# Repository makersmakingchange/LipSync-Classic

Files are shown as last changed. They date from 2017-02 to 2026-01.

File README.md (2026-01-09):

# LipSync Classic

> [!IMPORTANT]
**As of 2024-Feb-08, this version of the LipSync is now obsolete and has been replaced by the [LipSync 4](https://github.com/makersmakingchange/LipSync).** 

The LipSync Classic is an assistive technology device that allows quadriplegics and other people with limited hand function to use touchscreen mobile devices, tablets, and computers by manipulation of a mouth-operated joystick with integrated sip and puff controls. This is an Open-Source Hardware project, so the Lipsync can be made at the community level for less than $300.

## Compatibility 

 <table style="width:100%">
  <tr>
    <th>Operating Systems</th>
    <th>Version</th>
    <th>Release</th>
    <th>Additional Information</th>
  <tr>
    <td>iOS</td>
    <td>13.1</td>
    <td>September 19,2019</td>
    <td>Compatible with iPhone 7 and newer versions (Requires USB to Lightning or USB to USB-C Adapter)</td>
  </tr>
  <tr>
    <td>Windows</td>
    <td>XP,7,10</td>
    <td>2001</td>
    <td>Compatible with Windows XP and newer versions</td>
  </tr>
  <tr>
    <td>Android</td>
    <td>4-9</td>
    <td>Released 2013</td>
    <td>Compatible with Android 4 and newer versions (Requires USB On-The-Go)</td>
  </tr>
  <tr>
    <td>MacOS</td>
    <td>10</td>
    <td>Released 2000</td>
    <td>Compatible with Mac OS X 10.0 and newer versions</td>
  </tr>
  </table> 

## Download

 <table style="width:100%">
  <tr>
    <th>Resource</th>
    <th>Version</th>
    <th>Format</th>
    <th>Link</th>
  </tr>
    <tr>
    <td>LipSync All</td>
    <td>3.0</td>
    <td>ZIP</td>
    <td><a href="https://github.com/makersmakingchange/LipSync/archive/refs/heads/main.zip">LipSync.zip</a></td>
  </tr>
  <tr>
    <td>LipSync Assembly Guide</td>
    <td>1.6</td>
    <td>PDF</td>
    <td><a href="https://github.com/makersmakingchange/LipSync/blob/main/Documentation/LipSync_Assembly_Guide.pdf">LipSync_Assembly_Guide.pdf</a></td>
  </tr>
  <tr>
    <td>LipSync Startup Guide</td>
    <td>1.8</td>
    <td>PDF</td>
    <td><a href="https://github.com/makersmakingchange/LipSync/blob/main/Documentation/LipSync_Startup_Guide.pdf">LipSync_Startup_Guide.pdf</a></td>
  </tr>
  <tr>
    <td>LipSync User Guide</td>
    <td>1.3</td>
    <td>PDF</td>
    <td><a href="https://github.com/makersmakingchange/LipSync/blob/main/Documentation/LipSync_User_Guide.pdf">LipSync_User_Guide.pdf</a></td>
  </tr>
  <tr>
     <td>LipSync Mounting Guide</td>
     <td>1.0</td>
     <td>PDF</td>
     <td><a href="https://github.com/makersmakingchange/LipSync/blob/main/Documentation/LipSync_Mounting_Guide.pdf">LipSync_Mounting_Guide.pdf</a></td>
  </tr>
  <tr>
    <td>LipSync BOM (XLSX)</td>
    <td>September 1, 2021</td>
    <td>XLSX</td>
    <td><a href="https://github.com/makersmakingchange/LipSync/blob/main/Documentation/LipSync_BOM.xlsx">LipSync_BOM.xlsx</a></td>
  </tr>
  <tr>
    <td>LipSync BOM (CSV)</td>
    <td>September 1, 2021</td>
    <td>CSV</td>
    <td><a href="https://github.com/makersmakingchange/LipSync/blob/main/Documentation/LipSync_BOM.csv">LipSync_BOM.csv</a></td>
  </tr>
  <tr>
    <td>LipSync Firmware</td>
    <td>3.0</td>
    <td>INO</td>
    <td><a href="https://raw.githubusercontent.com/makersmakingchange/LipSync/main/Software/LipSync_Firmware/LipSync_Firmware.ino">LipSync_Firmware.ino</a></td>
  </tr>
  <tr>
    <td>LipSync Interface Board Layout</td>
    <td>2.71</td>
    <td>BRD</td>
    <td><a href="https://raw.githubusercontent.com/makersmakingchange/LipSync/main/Hardware/PCB_design/Eagle/LipSync_Interface_Board/LipSync_Interface_Board.brd">LipSync_Interface_Board.brd</a></td>
  </tr>
  <tr>
    <td>LipSync Interface Board Schematic</td>
    <td>2.71</td>
    <td>SCH</td>
    <td><a href="https://raw.githubusercontent.com/makersmakingchange/LipSync/main/Hardware/PCB_design/Eagle/LipSync_Interface_Board/LipSync_Interface_Board.sch">LipSync_Interface_Board.sch</a></td>
  </tr>
  <tr>
    <td>JLCPCB LipSync Interface Board Gerber</td>
    <td>2.71</td>
    <td>ZIP</td>
    <td><a href="https://github.com/makersmakingchange/LipSync/raw/main/Hardware/PCB_design/Gerber/LipSync_Interface_Board/JLCPCB_LipSync_Interface_Board.zip">JLCPCB_LipSync_Interface_Board.zip</a></td>
  </tr>
  <tr>
    <td>OSHPark LipSync Interface Board Gerber</td>
    <td>2.71</td>
    <td>ZIP</td>
    <td><a href="https://github.com/makersmakingchange/LipSync/raw/main/Hardware/PCB_design/Gerber/LipSync_Interface_Board/OSHPark_LipSync_Interface_Board.zip">OSHPark_LipSync_Interface_Board.zip</a></td>
  </tr>
  <tr>
    <td>PCBWay LipSync Interface Board Gerber</td>
    <td>2.71</td>
    <td>ZIP</td>
    <td><a href="https://github.com/makersmakingchange/LipSync/raw/main/Hardware/PCB_design/Gerber/LipSync_Interface_Board/PCBWay_LipSync_Interface_Board.zip">PCBWay_LipSync_Interface_Board.zip</a></td>
  </tr>
  <tr>
    <td>Seeed Fusion LipSync Interface Board Gerber</td>
    <td>2.71</td>
    <td>ZIP</td>
    <td><a href="https://github.com/makersmakingchange/LipSync/raw/main/Hardware/PCB_design/Gerber/LipSync_Interface_Board/Seeed_Fusion_LipSync_Interface_Board.zip">Seeed_Fusion_LipSync_Interface_Board.zip</a></td>
  </tr>
  <tr>
    <td rowspan="9">Housing_design</td>
    <td rowspan="9">3.0</td>
    <td rowspan="9">STL</td>
    <td><a href="https://github.com/makersmakingchange/LipSync/blob/main/Hardware/Housing_design/LipSync_Button.stl">LipSync_Button.STL</a></td>
  </tr>
  <tr>
  <td><a href="https://github.com/makersmakingchange/LipSync/blob/main/Hardware/Housing_design/LipSync_Front_Housing.STL">LipSync_Front_Housing.STL</a></td>
  </tr>
  <tr>
	<td><a href="https://github.com/makersmakingchange/LipSync/blob/main/Hardware/Housing_design/LipSync_Joystick_Base.STL">LipSync_Joystick_Base.STL</a></td>
</tr>
<tr>
  <td><a href="https://github.com/makersmakingchange/LipSync/blob/main/Hardware/Housing_design/LipSync_Joystick_Front.STL">LipSync_Joystick_Front.STL</a></td>
</tr>
<tr>
  <td><a href="https://github.com/makersmakingchange/LipSync/blob/main/Hardware/Housing_design/LipSync_Joystick_Rocker.STL">LipSync_Joystick_Rocker.STL</a></td>
</tr>
<tr>
    <td><a href="https://github.com/makersmakingchange/LipSync/blob/main/Hardware/Housing_design/Optional/LipSync_Joystick_Jig.STL">LipSync_Joystick_Jig.STL</a></td>
</tr>
<tr>
  <td><a href="https://github.com/makersmakingchange/LipSync/blob/main/Hardware/Housing_design/LipSync_Rear_Housing.STL">LipSync_Rear_Housing.STL</a></td>
</tr>
<tr>
  <td><a href="https://github.com/makersmakingchange/LipSync/blob/main/Hardware/Housing_design/3D_Print_Settings.txt">3D_Print_Settings.txt</a></td>
</tr>
</table> 

## Resources

<table style="width:100%">
  <tr>
    <th>Resource</th>
    <th>Link</th>
  </tr>
  <tr>
    <td>LipSync Firmware and Calibration Video</td>
    <td><a href="https://www.youtube.com/watch?v=RnpA24WH0Qk">Video</a></td>
  <tr>
    <td>LipSync Joystick Calibration Video</td>
    <td><a href="https://www.youtube.com/watch?v=Daf-54y6SBg">Video</a></td>
  </tr>
    <tr>
    <td>LipSync Build Video</td>
    <td><a href="https://www.youtube.com/watch?v=lBXpbkp5DW4&list=PLhoPg9bDvBR4CSFRfNbQ87ALnfaHOyM3C">Video</a></td>
  </tr>
</table> 

## License
Copyright (c) 2016-2024 Neil Squire / Makers Making Change.

This repository describes Open Hardware:
 - Everything needed or used to design, make, test, or prepare the LipSync Classic is licensed under the [CERN 2.0 Weakly Reciprocal license (CERN-OHL-W v2) or later](https://cern.ch/cern-ohl ) .
 - All software is under the [GNU General Public License v3.0 (GPL-3.0)](https://www.gnu.org/licenses/gpl.html).
 - Accompanying material such as instruction manuals, videos, and other copyrightable works that are useful but not necessary to design, make, test, or prepare the LipSync are published under a [Creative Commons Attribution-ShareAlike 4.0 license (CC BY-SA 4.0)](https://creativecommons.org/licenses/by-sa/4.0/) .

You may redistribute and modify this documentation and make products using it under the terms of the [CERN-OHL-W v2](https://cern.ch/cern-ohl).
This documentation is distributed WITHOUT ANY EXPRESS OR IMPLIED WARRANTY, INCLUDING OF MERCHANTABILITY, SATISFACTORY QUALITY AND FITNESS FOR A PARTICULAR PURPOSE.
Please see the CERN-OHL-W v2 for applicable conditions.

Source Location: https://github.com/makersmakingchange/LipSync-Classic

## Attribution

The LipSync was designed by Neil Squire Society / Makers Making Change. The initial development of a 3D printable LipSync was supported by the Google Impact Challenge: Disabilities grant from Google.org. Further development was supported through the Government of Canada's Innovation Science and Economic Development Assistive Technology Program. These and other funders have also enabled Neil Squire / Makers Making Change to deploy numerous LipSyncs to users at reduced cost.

The LipSync firmware utilizes the Arduino development platform, an open-source electronics platform based on easy-to-use hardware and software. Arduino is developed and maintained by the Arduino community, and the project wouldn't be possible without their contributions. Arduino is a registered trademark of Arduino AG. For more information about Arduino and to contribute to the community, visit the official Arduino website at www.arduino.cc.

### Contributors

Numerous Neil Squire staff, users, and volunteers have contribued to the development of the LipSync. 

 - Derrick Andrews
 - Ivan Gourlay
 - Jake McIvor
 - Kristina Mok
 - Milad Hajihassan

----

<!-- ABOUT MMC START -->
## About Makers Making Change
[Makers Making Change Logo](https://www.makersmakingchange.com/)

Makers Making Change is a program of [Neil Squire](https://www.neilsquire.ca/), a Canadian non-profit that uses technology, knowledge, and passion to empower people with disabilities.

Makers Making Change leverages the capacity of community based Makers, Disability Professionals and Volunteers to develop and deliver affordable Open Source Assistive Technologies.

 - Website: [www.MakersMakingChange.com](https://www.makersmakingchange.com/)
 - GitHub: [makersmakingchange](https://github.com/makersmakingchange)
 - Bluesky: [@makersmakingchange.bsky.social](https://bsky.app/profile/makersmakingchange.bsky.social)
 - Instagram: [@makersmakingchange](https://www.instagram.com/makersmakingchange)
 - Facebook: [makersmakechange](https://www.facebook.com/makersmakechange)
 - LinkedIn: [Neil Squire Society](https://www.linkedin.com/company/neil-squire-society/)
 - Thingiverse: [makersmakingchange](https://www.thingiverse.com/makersmakingchange/about)
 - Printables: [MakersMakingChange](https://www.printables.com/@MakersMakingChange)

### Contact Us
For technical questions, to get involved, or to share your experience we encourage you to [visit our website](https://www.makersmakingchange.com/) or [contact us](https://www.makersmakingchange.com/s/contact).
<!-- ABOUT MMC END -->

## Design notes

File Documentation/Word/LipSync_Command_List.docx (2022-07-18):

## LipSync Mouse Command List

Command | Success Response | Failure Response | Description
SETTINGS | SUCCESS,0:SETTINGS | FAIL,{N}: Command | Enter Settings mode
EXIT | SUCCESS,0:EXIT | FAIL,{N}: Command | Exit Settings mode
MN,0:0 | SUCCESS,0:MN,0:1 | FAIL,{N}:Command | Get Model number (1=Mouse)
VN,0:0 | SUCCESS,0:VN,0:V{N.NN} | FAIL,{N}:Command | Get version number (V{N.NN})
SS,0:0 | SUCCESS,0:SS,0:{Cursor Speed Level} | FAIL,{N}:Command | Get the mouse cursor speed value (Level)
SS,1:{Cursor Speed Level:0-10} | SUCCESS,0:SS,1:{Cursor Speed Level} | FAIL,{N}:Command | Set the mouse cursor speed value (Level)
| MANUAL,0:SS,1:{Cursor Speed Level} | | Set the mouse cursor speed value (Level)
PT,0:0 | SUCCESS,0:PT,0:{Threshold 5% to 50%}:{Nominal Pressure V*100} | FAIL,{N}:Command | Get puff pressure threshold (threshold 5% to 50%) (Nominal Pressure)
PT,1:{threshold 10% to 50%} | SUCCESS,0:PT,1:{Threshold 5% to 50%}:{ Nominal Pressure V*100} | FAIL,{N}:Command | Set puff pressure threshold (threshold 5% to 50%) (Nominal Pressure)
ST,0:0 | SUCCESS,0:PT,0:{Threshold 5% to 50%}:{Nominal Pressure V*100} | FAIL,{N}:Command | Get sip pressure threshold (threshold 5% to 50%) (Nominal Pressure)
ST,1:{threshold 5% to 50%} | SUCCESS,0:PT,1:{Threshold 5% to 50%}:{ Nominal Pressure V*100} | FAIL,{N}:Command | Set sip pressure threshold (threshold 5% to 50%) (Nominal Pressure)
PV,0:0 | SUCCESS,0:PV,0:{Nominal Pressure} | FAIL,{N}:Command | Get pressure value (Nominal Pressure)
RA,0:0 | SUCCESS,0:RA,0:{Rotation Angle} | FAIL,{N}:Command | Get rotation angle (deg)
RA,1:{Angle: 0-359} | SUCCESS,0:RA,1:{Rotation Angle} | FAIL,{N}:Command | Set rotation angle (0,90,180,270 deg)
DM,0:0 | SUCCESS,0:DM,0:{Debug Mode} | FAIL,{N}:Command | Get debug mode value ( 0=debug mode disabled,1=debug mode enabled)
DM,1:0 | SUCCESS,0:DM,1:0 | FAIL,{N}:Command | Set debug mode value to 0 (Disabled)
DM,1:1 | SUCCESS,0:DM,1:1 | FAIL,{N}:Command | Set debug mode value to 1 (Enabled)
| LOG,1:{0,0,0,xHighNeutral,xLowNeutral,yHighNeutral,yLowNeutral} | | Log initialization values once if debug mode is enabled
| LOG,2:{0,0,0,xHighMax,xLowMax,yHighMax,yLowMax} | | Log calibration values once if debug mode is enabled
| LOG,3:{x,y,action,xHigh,xLow,yHigh,yLow} | | Log cursor and FSR values if debug mode is enabled until debug mode is disabled
IN,0:0 | SUCCESS,0:IN,0:{xHighNeutral,xLowNeutral,yHighNeutral,yLowNeutral} | FAIL,{N}:Command | Get joystick initialization values (xHighNeutral,xLowNeutral,yHighNeutral,yLowNeutral)
IN,1:1 | SUCCESS,0:IN,1:{xHighNeutral,xLowNeutral,yHighNeutral,yLowNeutral} | FAIL,{N}:Command | Perform joystick initialization using command (xHighNeutral,xLowNeutral,yHighNeutral,yLowNeutral)
| MANUAL,0:IN,1:{xHighNeutral,xLowNeutral,yHighNeutral,yLowNeutral} | | Perform joystick initialization using push button or sip/puff (xHighNeutral, xLowNeutral,yHighNeutral,yLowNeutral)
JV,0:0 | SUCCESS,0:JV,0:{xHigh,xLow,yHigh,yLow} | FAIL,{N}:Command | Get joystick FSR values: {xHigh,xLow,yHigh,yLow}
CA,0:0 | SUCCESS,0:CA,0:{xHighMax,xLowMax,yHighMax,yLowMax} | FAIL,{N}:Command | Get joystick calibration values (xHighMax,xLowMax,yHighMax,yLowMax)
CA,1:1 | SUCCESS,0:CA,1:0 | FAIL,{N}:Command | Perform joystick calibration using command
| SUCCESS,0:CA,1:1 | FAIL,{N}:Command | Perform joystick calibration using command (Step 1)
| SUCCESS,0:CA,1:2 | FAIL,{N}:Command | Perform joystick calibration using command (Step 2)
| SUCCESS,0:CA,1:3 | FAIL,{N}:Command | Perform joystick calibration using command (Step 3)
| SUCCESS,0:CA,1:4 | FAIL,{N}:Command | Perform joystick calibration using command (Step 4)
| SUCCESS,0:CA,1:5:{xHighMax,xLowMax,yHighMax,yLowMax} | FAIL,{N}:Command | Perform joystick calibration using command (Step 5) (xHighMax,xLowMax,yHighMax,yLowMax)
| MANUAL,0:CA,1:0 | | Perform joystick calibration using push button
| MANUAL,0:CA,1:1 | | Perform joystick calibration using push button (Step 1)
| MANUAL,0:CA,1:2 | | Perform joystick calibration using push button (Step 2)
| MANUAL,0:CA,1:3 | | Perform joystick calibration using push button (Step 3)
| MANUAL,0:CA,1:4 | | Perform joystick calibration using push button (Step 4)
| MANUAL,0:CA,1:5:{xHighMax,xLowMax,yHighMax,yLowMax} | | Perform joystick calibration using push button (Step 5) (xHighMax,xLowMax,yHighMax,yLowMax)
CT,0:0 | SUCCESS,0:CT,0:{changeTolerance} | FAIL,{N}:Command | Get drift change tolerance value
CT,1: {Change Tolerance: 0-30} | SUCCESS,0:CT,1:{changeTolerance} | FAIL,{N}:Command | Set drift change tolerance value
MP,0:0 | SUCCESS,0:MP,0:{NNNNNN} | FAIL,{N}:Command | Get Button mapping ( Example: SUCCESS,0:MP,0:123465)
MP,1: {NNNNNN} | SUCCESS,0:MP,1:{NNNNNN} | FAIL,{N}:Command | Set Button mapping ( Example: MP,1:123465)
SL,0:0 | SUCCESS,0:SL,0:{Scroll Speed Level} | FAIL,{N}:Command | Get the mouse scroll speed value (Level)
SL,1:{Scroll Speed Level:0-10} | SUCCESS,0:SL,1:{Scroll Speed Level} | FAIL,{N}:Command | Set the mouse scroll speed value (Level)
FR,1:{Rest Type: 0-1} | SUCCESS,0:FR,1:{Reset Type: 0-1} | FAIL,{N}:Command | Perform factory reset (0 = Hard Reset , 1 = Soft Reset)

## API Format

The API format which includes the end-point, command ,and the parameters.

## Response Code

Response Status | Response Code | Description
SUCCESS | 0 | The command has successfully performed.
FAIL | 0 | The serial API mode is not enabled. Please enter the serial API mode.
FAIL | 1 | The requested command does not exist. Returns the response code and the requested parameter.
FAIL | 2 | The requested command exists, but the entered parameter is in incorrect format. Returns the response code and the requested parameter.
FAIL | 3 | The requested command exists, but the entered parameter is out of range. Returns the response code and the current value stored in the EEPROM.

## Input Actions

Input Action | Description
Short Puff | < 3 seconds
Short Sip | < 3 seconds
Long Puff | 3-5 seconds
Long Sip | 3-5 seconds
Very Long Puff | > 5 seconds
Very Long Sip | > 5 seconds

## Output Actions Options

Action Number | Output Action | Description
0 | (No action) | No action
1 | Left Click | Presses and immediately releases a left click.
2 | Right Click | Presses and immediately releases a right click.
3 | Drag Mode | Initiates drag mode. Left click is pressed and held down. Cancelled with short puff or short sip.
4 | Scroll Mode | Initiates Scroll mode. Vertical motion of joystick generates mouse scroll wheel movements. Cancelled with short puff or short sip.
5 | Middle Click | Presses and immediately releases a middle click.
6 | Center Reset | Initiates center reset routine to set joystick center position.
7 | Calibration | Initiates joystick calibration routine to set joystick limits and reset joystick center.

## Action Mapping

Input Action | LipSync Mouse Action
Short Puff | 1 : Left Click
Short Sip | 2 : Right Click
Long Puff | 3: Drag Mode
Long Sip | 4 : Scroll Mode
Very Long Puff | 6: Center Reset
Very Long Sip | 0: No Action

## Example

INPUT | RESPONSE | ACTION
SETTINGS | SUCCESS,0:SETTINGS | LipSync Ready for API Command
VN,0:0 | SUCCESS,0:VN,0:30 | LipSync return firmware version 3.0

INPUT | RESPONSE | ACTION
SETTINGS | SUCCESS,0:SETTINGS | LipSync Ready for API Command
PT,0:0 | SUCCESS,0:PT,0:10 | LipSync return current puff pressure threshold of 10%
PT,1:20 | FAIL,0:PT,1:20 | (Attempt to set puff pressure threshold failed – need to resend SETTINGS for each command)
SETTINGS | SUCCESS,0:SETTINGS | LipSync Ready for API Command
PT,1:20 | SUCCESS,0:PT,1:20:266 | LipSync set new puff pressure threshold of 20% and returned current nominal pressure of

Makers Making Change LipSync Mouse Command List

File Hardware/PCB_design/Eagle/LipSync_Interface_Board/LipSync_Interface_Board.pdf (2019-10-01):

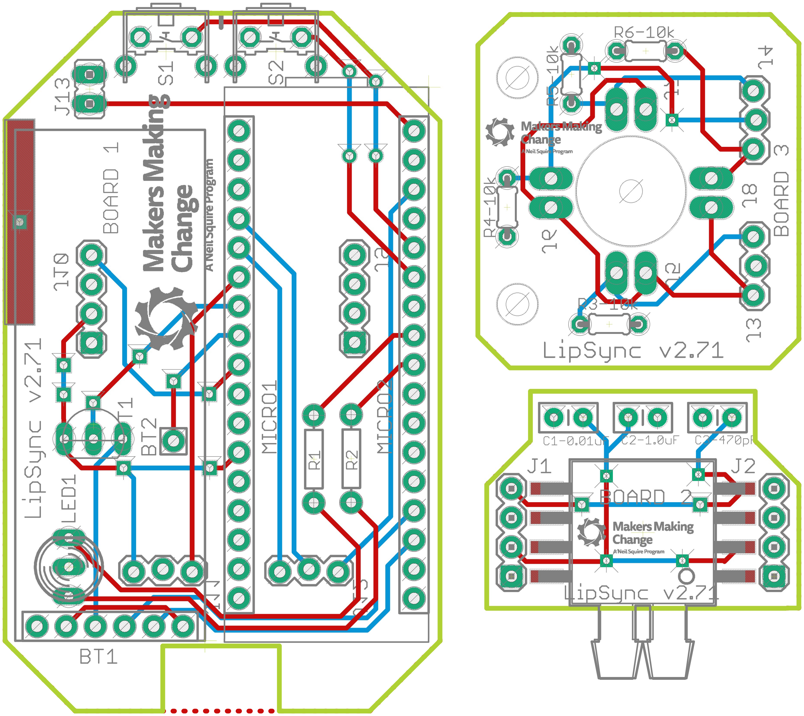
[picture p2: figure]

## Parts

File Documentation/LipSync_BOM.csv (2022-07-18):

Qty | Component | Component name (September 1, 2021) | Line Item | Manufacturer | COO | MPN | SKU | SKU | SKU | SKU | SKU | SKU | SKU | SKU | URL ( Canada ) | URL ( United States )
 |  |  |  |  |  |  | Digi-Key | Mouser | Qosina | Cole-Parmer | Lee Spring | U.S. Plastic Corp. | B&H Photo | Amazon
1 | Required | Arduino Micro | A000053 | Arduino | Italy | A000053 | 1050-1066-ND | 782-A000053 |  |  |  |  |  |  | https://www.digikey.ca/product-detail/en/arduino/A000053/1050-1066-ND | https://www.digikey.com/product-detail/en/arduino/A000053/1050-1066-ND
2 | Required | Right Angle Push Button | "431256058736" | Würth Elektronik | China | "431256058736" | 431256058736-ND |  |  |  |  |  |  |  | http://www.digikey.ca/product-detail/en/wurth-electronics-inc/431256058736/431256058736-ND | https://www.digikey.com/product-detail/en/wurth-electronics-inc/431256058736/431256058736-ND
2 | Required | 300 Ohm 1/4W Axial Through-Hole Resistor | CF14JT300R | Stackpole Electronics | China | CF14JT300R | CF14JT300RCT-ND |  |  |  |  |  |  |  | https://www.digikey.ca/product-detail/en/stackpole-electronics-inc/CF14JT300R/CF14JT300RCT-ND | https://www.digikey.com/product-detail/en/stackpole-electronics-inc/CF14JT300R/CF14JT300RCT-ND
4 | Required | 10k Ohm 1/4W Mini Axial Through-Hole Resistor | CFM14JT10K0 | Stackpole Electronics | China | CFM14JT10K0 | S10KQCT-ND |  |  |  |  |  |  |  | https://www.digikey.ca/product-detail/en/stackpole-electronics-inc/CFM14JT10K0/S10KQCT-ND/ | https://www.digikey.com/product-detail/en/stackpole-electronics-inc/CFM14JT10K0/S10KQCT-ND/
1 | Required | Pressure Transducer | MPXV7002DPT1 | NXP Semiconductors | Malaysia | MPXV7002DPT1 | MPXV7002DPT1CT-ND | 841-MPXV7002DP |  |  |  |  |  |  | https://www.digikey.ca/product-detail/en/freescale-semiconductor-nxp/MPXV7002DPT1/MPXV7002DPT1CT-ND | https://www.digikey.com/product-detail/en/freescale-semiconductor-nxp/MPXV7002DPT1/MPXV7002DPT1CT-ND
1 | Required | 0.01 uF Ceramic Through-Hole Radial Capacitor | C315C103K5R5TA | KEMET | Mexico | C315C103K5R5TA | 399-4148-ND | 80-C315C103K5R |  |  |  |  |  |  | http://www.digikey.ca/product-detail/en/kemet/C315C103K5R5TA7303/399-9858-1-ND | http://www.digikey.com/product-detail/en/kemet/C315C103K5R5TA7303/399-9858-1-ND
1 | Required | 1.0 uF Ceramic Through-Hole Radial Capacitor | C315C105K3R5TA | KEMET | Mexico | C315C105K3R5TA | 399-9714-ND | 80-C315C105K3R |  |  |  |  |  |  | http://www.digikey.ca/product-detail/en/kemet/C315C105K3R5TA/399-9714-ND | http://www.digikey.com/product-detail/en/kemet/C315C105K3R5TA/399-9714-ND
1 | Required | 470 pF Ceramic Through-Hole Radial Capacitor | C315C471K5R5TA | KEMET | Mexico | C315C471K5R5TA | 399-9740-ND | 80-C315C471K5R |  |  |  |  |  |  | http://www.digikey.ca/product-detail/en/kemet/C315C471K5R5TA/399-9740-ND | http://www.digikey.com/product-detail/en/kemet/C315C471K5R5TA/399-9740-ND
2 | Required | 17-Position Straight Female Through-Hole Headers | PPPC171LFBN-RC | Sullins | Taiwan | PPPC171LFBN-RC | S7050-ND |  |  |  |  |  |  |  | http://www.digikey.ca/product-detail/en/sullins-connector-solutions/PPPC171LFBN-RC/S7050-ND | http://www.digikey.com/product-detail/en/sullins-connector-solutions/PPPC171LFBN-RC/S7050-ND
2 | Required | 3-Position Right Angle Male Through-Hole Header | 22-05-2031 | Molex | Mexico | 22-05-2031 | WM4101-ND |  |  |  |  |  |  |  | https://www.digikey.ca/product-detail/en/molex-connector-corporation/22-05-2031/WM4101-ND/ | https://www.digikey.com/product-detail/en/molex-connector-corporation/22-05-2031/WM4101-ND/
2 | Required | 3-Position Straight Female Through-Hole Header | 801-87-003-10-001101 | Preci-Dip | Switzerland | 801-87-003-10-001101 | 1212-1180-ND |  |  |  |  |  |  |  | https://www.digikey.ca/product-detail/en/preci-dip/801-87-003-10-001101/1212-1180-ND | https://www.digikey.com/product-detail/en/preci-dip/801-87-003-10-001101/1212-1180-ND
2 | Required | 4-Position Straight Female Through-Hole Header | PPPC041LFBN-RC | Sullins | Taiwan | PPPC041LFBN-RC | S7037-ND |  |  |  |  |  |  |  | http://www.digikey.ca/product-detail/en/sullins-connector-solutions/PPPC041LFBN-RC/S7037-ND | https://www.digikey.com/product-detail/en/sullins-connector-solutions/PPPC041LFBN-RC/S7037-ND
1 | Required | 40-Position Breakaway Straight Male Through-Hole Headers | PRPC040SAAN-RC | Sullins | Taiwan | PRPC040SAAN-RC | S1011EC-40-ND |  |  |  |  |  |  |  | http://www.digikey.ca/product-detail/en/sullins-connector-solutions/PRPC040SAAN-RC/S1011EC-40-ND | http://www.digikey.com/product-detail/en/sullins-connector-solutions/PRPC040SAAN-RC/S1011EC-40-ND
1 | Required | 5mm Bi-Color Through-Hole LED | MV5437 | Everlight Electronics Co Ltd | China | MV5437 | 1080-1109-ND |  |  |  |  |  |  |  | https://www.digikey.ca/product-detail/en/everlight-electronics-co-ltd/MV5437/1080-1109-ND/2675600 | https://www.digikey.com/product-detail/en/everlight-electronics-co-ltd/MV5437/1080-1109-ND/2675601
1 | Required | Jumper Shunt Connector | SSC02SYAN | Sullins | Taiwan | SSC02SYAN | S9002-ND |  |  |  |  |  |  |  | https://www.digikey.ca/product-detail/en/sullins-connector-solutions/SPC02SYAN/S9002-ND | https://www.digikey.com/product-detail/en/sullins-connector-solutions/SPC02SYAN/S9002-ND
1 | Required | 2N3906 PNP-type Through-Hole Transistor | 2N3906TFR | Fairchild Semiconductor | China | 2N3906TFR | 2N3906D26ZCT-ND |  |  |  |  |  |  |  | http://www.digikey.ca/product-detail/en/fairchild-on-semiconductor/2N3906TFR/2N3906D26ZCT-ND | http://www.digikey.com/product-detail/en/fairchild-on-semiconductor/2N3906TFR/2N3906D26ZCT-ND
1 | Required | 6-Position Straight Female Through-Hole Header | PPPC061LFBN-RC | Sullins | Taiwan | PPPC061LFBN-RC | S7039-ND |  |  |  |  |  |  |  | https://www.digikey.ca/product-detail/en/sullins-connector-solutions/PPPC061LFBN-RC/S7039-ND | https://www.digikey.com/product-detail/en/sullins-connector-solutions/PPPC061LFBN-RC/S7039-ND
1 | Required | Sip and Puff Mouthpiece | "11648" | Qosina | USA | "80102" |  |  | "80102" |  |  |  |  |  | https://www.qosina.com/stepped-male-luer-lock-connector-80102 | https://www.qosina.com/stepped-male-luer-lock-connector-80102
1 | Required | Filter PTFE Hydrophobic 17 mm, 0.2 Micron | "28213" | Qosina | USA | "28213" |  |  | "28213" |  |  |  |  |  | http://www.qosina.com/hydrophobic-filter-with-female-luer-lock-inlet-male-luer-lock-outlet-28213 | http://www.qosina.com/hydrophobic-filter-with-female-luer-lock-inlet-male-luer-lock-outlet-28213
1 | Required | Luer Lock Fitting | RK-45508-32 | Cole-Parmer | USA | RK-45508-32 |  |  |  | RK-45508-32 |  |  |  |  | https://www.coleparmer.ca/i/cole-parmer-female-luer-bulkhead-1-4-28-unf-thread-to-3-32-hose-barb-pp-25-pk/4550832 | https://www.coleparmer.ca/i/cole-parmer-female-luer-bulkhead-1-4-28-unf-thread-to-3-32-hose-barb-pp-25-pk/4550832
4 | Required | Force Resistive Sensor | 30-49649 | Interlink Electronics | China | 30-49649 | 1027-1000-ND |  |  |  |  |  |  |  | http://www.digikey.ca/product-detail/en/interlink-electronics/30-49649/1027-1000-ND | http://www.digikey.com/product-detail/en/interlink-electronics/30-49649/1027-1000-ND
4 | Required | Screws Phillips Head M3 | NMS-308 | Würth Elektronik | China | 97790803211 | 732-13710-ND |  |  |  |  |  |  |  | https://www.digikey.ca/en/products/detail/w%C3%BCrth-elektronik/97790803211/10056393 | https://www.digikey.com/en/products/detail/w%C3%BCrth-elektronik/97790803211/10056393
6 | Required | Compression Spring | LC 016C 03 S | Lee Spring | China | LC 016C 03 S |  |  |  |  | LC 016C 03 S |  |  |  | https://www.leespring.com/compression-springs?search=LC016C03S | https://www.leespring.com/compression-springs?search=LC016C03S
2 | Required | Standoff M3 10mm | "25501" | Keystone | USA | "25501" | 36-25501-ND | 534-25501 |  |  |  |  |  |  | http://www.digikey.ca/product-detail/en/keystone-electronics/25501/36-25501-ND/ | http://www.digikey.com/product-detail/en/keystone-electronics/25501/36-25501-ND/
2 | Required | Standoff M3 15mm | "25503" | Keystone | USA | "25503" | 36-25503-ND | 534-25503 |  |  |  |  |  |  | http://www.digikey.ca/product-detail/en/keystone-electronics/25503/36-25503-ND/ | http://www.digikey.com/product-detail/en/keystone-electronics/25503/36-25503-ND/
1 | Required | Luer Lock Nut | 45509-04 | Cole-Parmer | USA | 45509-04 |  |  |  | 45509-04 |  |  |  |  | https://www.coleparmer.ca/i/cole-parmer-panel-mount-lock-nut-1-4-28-unf-black-nylon-25-pk/4550904 | https://www.coleparmer.ca/i/cole-parmer-panel-mount-lock-nut-1-4-28-unf-black-nylon-25-pk/4550904
4 | Required | Bumper | SJ-5003 (BLACK) | 3M | USA | SJ-5003 (BLACK) | SJ5003-0-ND | 517-SJ-5003BK |  |  |  |  |  |  | https://www.mouser.ca/ProductDetail/3M-Electronic-Specialty/SJ-5003-BLACK?qs=sGAEpiMZZMvlOED0T0kTWubpGv7E7tyx | https://www.digikey.com/product-detail/en/3m/SJ-5003-(BLACK)/SJ5003-0-ND/102574
4 | Required | Nut M3 | 4708 | Keystone Electronics | Taiwan | 4708 | 36-4708-ND |  |  |  |  |  |  |  | https://www.digikey.ca/product-detail/en/keystone-electronics/4708/36-4708-ND/4499301 | https://www.digikey.com/product-detail/en/keystone-electronics/4708/36-4708-ND/4499301
1 | Required | Tubing Tygon 3350 3/32" ID x 45mm | "57289" | Tygon® | USA | "57289" |  |  |  |  |  | "57289" |  |  | http://www.usplastic.com/catalog/item.aspx?itemid=31562&catid=864 | http://www.usplastic.com/catalog/item.aspx?itemid=31562&catid=864
2 | Required | Light Pipe | 51513030250F | Dialight | Malaysia | 51513030250F | 350-3746-ND | 645-515-1303-0250F |  |  |  |  |  |  | http://www.mouser.com/search/ProductDetail.aspx?r=645-515-1303-0250F | http://www.mouser.com/search/ProductDetail.aspx?r=645-515-1303-0250F
1 | Required | Threaded Insert 5/8”-27 | M-11 | WindTech | USA | M-11 |  |  |  |  |  |  | WIM11 |  | https://www.bhphotovideo.com/c/product/850285-REG/windtech_m_11_5_8_27_f_to_1_2_m_npt.html | https://www.adorama.com/wtm11.html
1 | Required | Threaded Adapter 5/8"-27 | Mic Adapter | CAMVATE | China | Mic Adapter |  |  |  |  |  |  |  | Mic Adapter | https://www.amazon.com/CAMVATE-Female-Male-Piece-Adapter/dp/B01GWVQ022 | https://www.amazon.com/CAMVATE-Female-Male-Piece-Adapter/dp/B01GWVQ022
1 | Required | USB Cable 3' or 6' | UUSBHAUB3RA | Startech | China | UUSBHAUB3RA |  |  |  |  |  |  |  | USB Cable 3' or 6' | https://www.amazon.ca/Startech-Com-UUSBHAUB3RA-Micro-Cable-Right/dp/B001AR4NC8 | https://www.amazon.com/StarTech-com-Micro-USB-Cable-UUSBHAUB3RA/dp/B001AR4NC8 | https://www.amazon.com/gp/huc/view.html?ie=UTF8&newItems=C50dc2962-6371-4880-bf41-06ac5db860d9%2C1 | https://www.amazon.com/gp/product/B01M18TDO1/ref=ox_sc_act_title_2?smid=A21TE5CLHZDYA7&psc=1
1 | Required | USB Splitter | USB Splitter | JIUWU | China | USB Splitter |  |  |  |  |  |  |  | USB Splitter | https://www.amazon.ca/Wpeng-Female-degree-Micro-Splitter/dp/B01M5F47SY | https://www.amazon.com/Micro-Female-Cable-Power-Splitter/dp/B00NSBVNCM
1 | Required | Cable Tie | 298-1021-ND | Panduit Corp | Singapore | PLT.6SM-M |  | 644-PLT.6SM-M |  |  |  |  |  |  | https://www.mouser.ca/ProductDetail/Panduit/PLT6SM-M | https://www.mouser.com/ProductDetail/Panduit/PLT6SM-M
1 | Optional | Magic Arm 11" and Clamp | ZC462800 | YKS / GkGk | China | ZC462800 |  |  |  |  |  |  |  | Magic Arm 11" and Clamp | https://www.amazon.com/GkGk-Articulating-Friction-Adjustable-Monitor/dp/B017HKJVL4/ | https://www.amazon.com/GkGk-Articulating-Friction-Adjustable-Monitor/dp/B017HKJVL4/

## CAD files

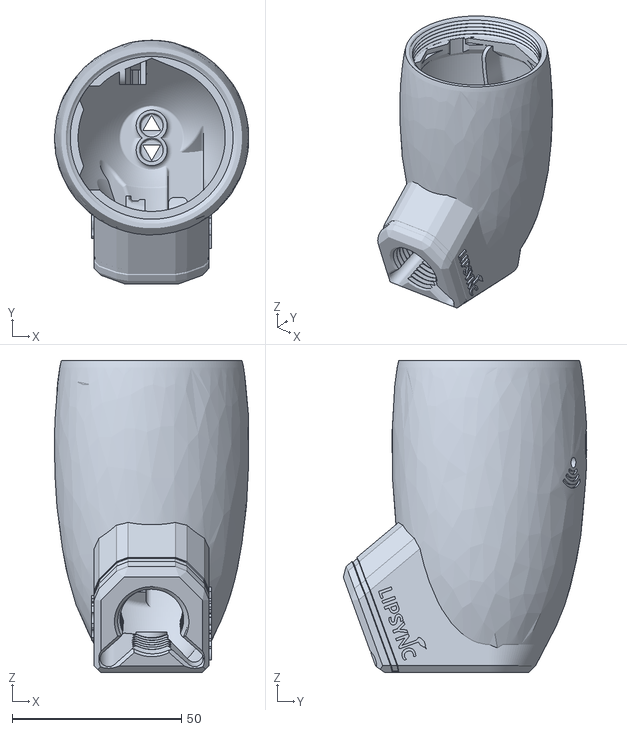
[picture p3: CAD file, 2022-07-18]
Hardware/Housing_design/LipSync_Rear_Housing.STL
57.5 x 72.0 x 92.2

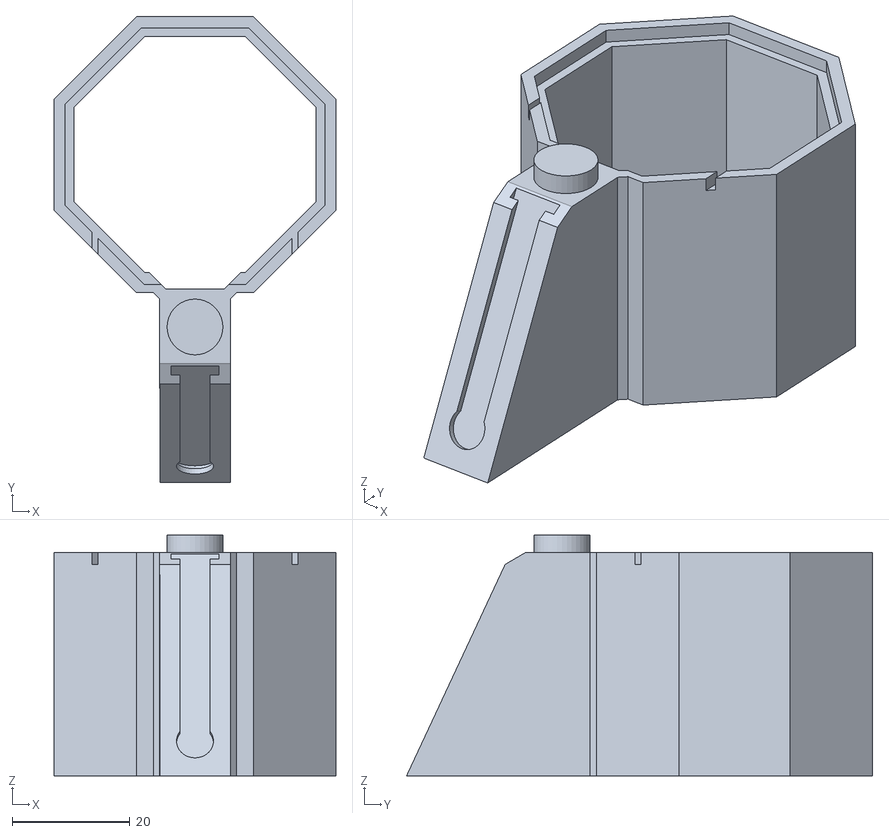
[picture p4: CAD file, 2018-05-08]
Hardware/Housing_design/Optional/LipSync_Joystick_Jig.STL
48.0 x 79.3 x 41.0

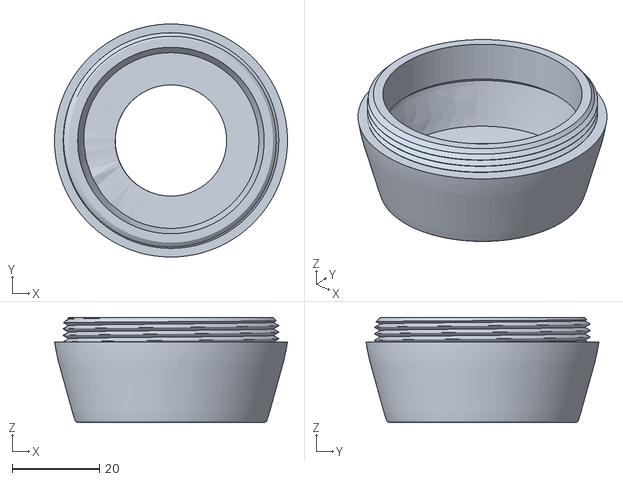
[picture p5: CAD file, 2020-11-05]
Hardware/Housing_design/LipSync_Front_Housing.STL
53.4 x 53.4 x 24.1

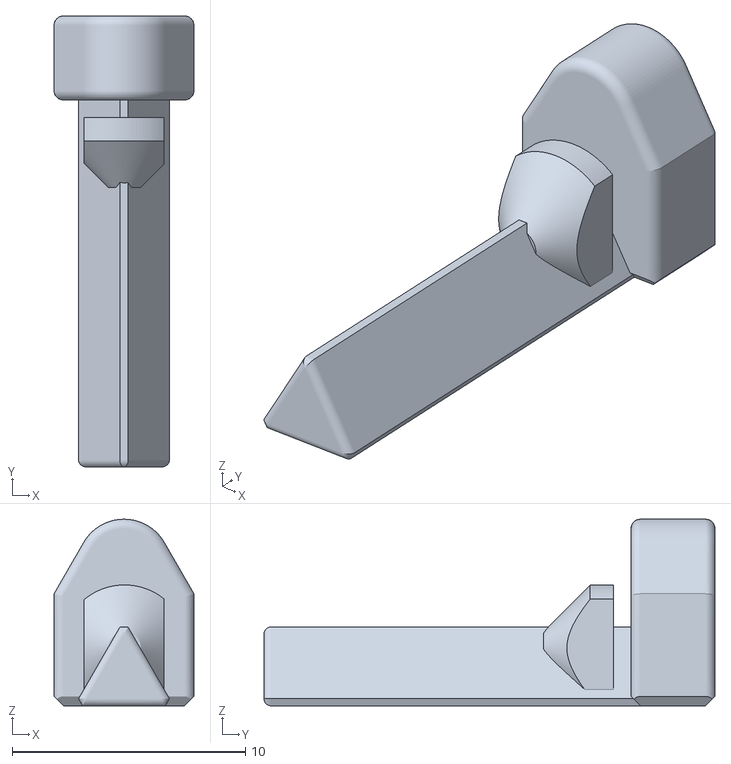
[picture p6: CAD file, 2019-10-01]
Hardware/Housing_design/LipSync_Button.stl
6.00 x 19.3 x 8.00

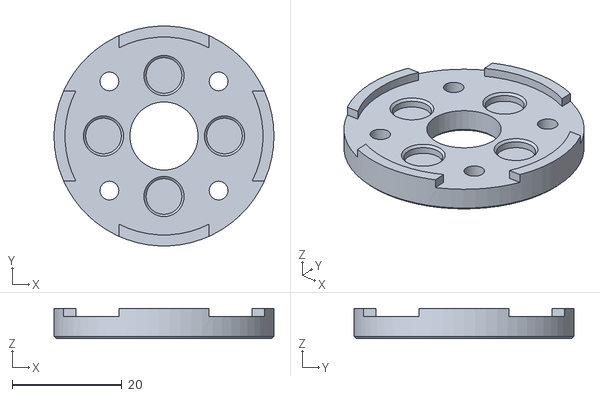
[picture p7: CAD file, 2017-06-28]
Hardware/Housing_design/LipSync_Joystick_Front.STL
40.0 x 39.9 x 5.50

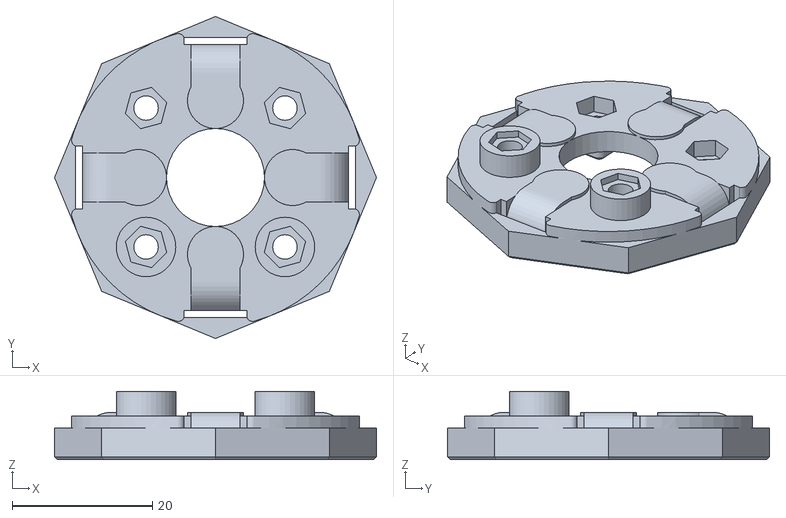
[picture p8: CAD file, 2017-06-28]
Hardware/Housing_design/LipSync_Joystick_Base.STL
46.0 x 46.0 x 9.75

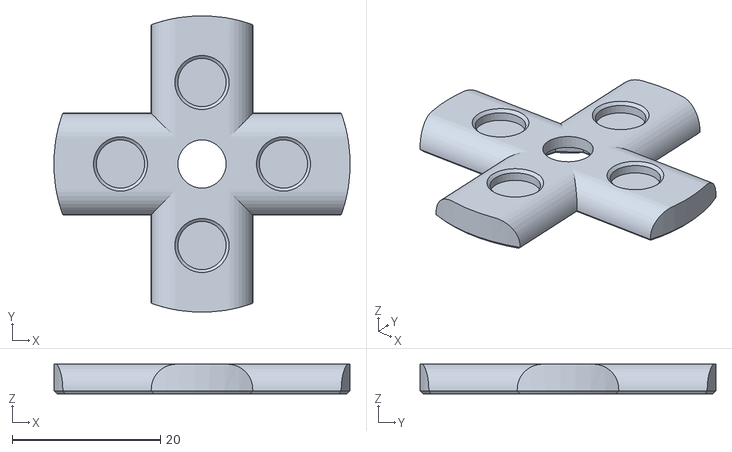
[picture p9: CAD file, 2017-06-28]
Hardware/Housing_design/LipSync_Joystick_Rocker.STL
40.0 x 40.0 x 4.00

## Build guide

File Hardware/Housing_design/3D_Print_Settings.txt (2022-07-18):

Print all components in orientation of STL file. Parts are designed to print with a 0.40 mm nozzle. Neutral, non-obtrusive filament colors (e.g. black, grey, white) are preferred for the rear housing and front housing unless the user requests otherwise. 

----------------------------
First print:
LipSync_Rear_Housing

Infill: 20%
Layer Height: 0.2mm
Support Material: No
Raft: No
Walls: 3
----------------------------

----------------------------
Second print:
1X LipSync_Front_Housing
2X LipSync_Button 
1X LipSync_Joystick_Stand (Optional; Recommended)

Infill: 20%
Layer Height: 0.2mm
Support Material: No
Raft: No
----------------------------

----------------------------
Third print:
1X LipSync_Joystick_Front_Plate
1X LipSync_Joystick_Rocker
1X LipSync_Joystick_Base

Infill: 50%
Layer Height: 0.2mm
Support Material: Yes
Raft: No
----------------------------

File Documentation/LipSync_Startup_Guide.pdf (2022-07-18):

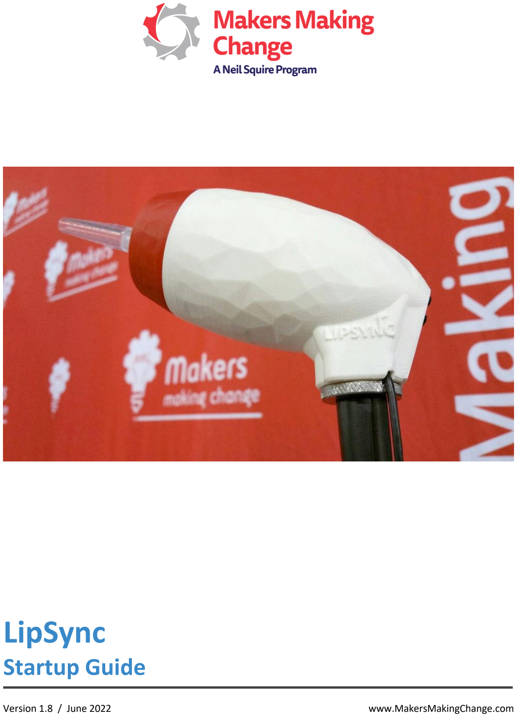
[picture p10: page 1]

# LipSync

# Startup Guide

Version 1.

8 / June 202

2 | www.MakersMakingChange.com

# Table of Contents

What Do You Get? | 3
Types of LipSync | 3
Mounting | 4
Device Compatibility | 5
Powering the LipSync | 5
Connecting the LipSync to a Device | 6
On-Screen Controls | 7
Functions | 8
Speed Control | 9
Cleaning the Mouthpiece and Filter | 10
Cleaning the LipSync Shell | 11
Joystick Calibration | 12 (https://neilsquiresoc.sharepoint.com/sites/MMC-RD/Shared%20Documents/Server/AT%20Projects%20-%20Internal/LipSync/Documentation/LipSync_Startup_Guide%20v1.6%20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)

# About the LipSync

The LipSync is a mouth operated joystick that allows a person who has limited or no control of their hands and arms

to control a cursor on a mobile phone, tablet or computer using only head movement. It is an open source assistive

technology design by Makers Making Change, a program of the Neil Squire Society that connects volunteer makers

with people with disabilities to create more affordable assistive technology.

Open source designs are freely released by their creators for people to make for themselves, modify or incorporate

in their own designs for free. Join the Makers Making Change to help people in your community:

http://www.makersmakingchange.com

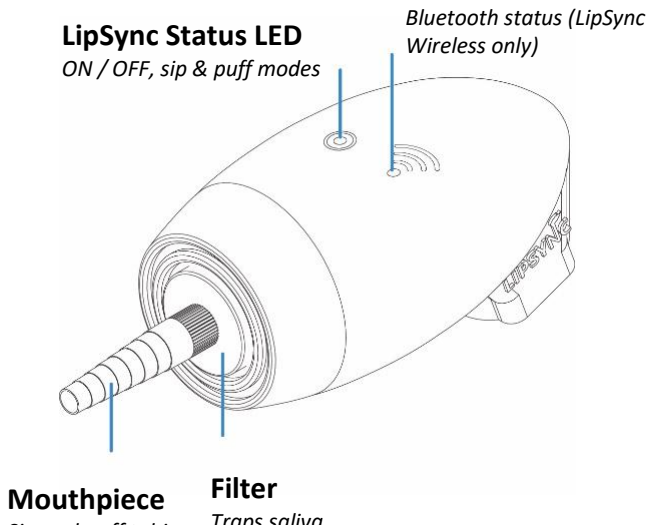
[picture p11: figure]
LipSync Status LED; ON / OFF, sip & puff modes; Bluetooth status (LipSync Wireless only); Filter; Mouthpiece

Parts of the LipSync

### What Do You Get?


### Types of LipSync

| Description | Connection Type
LipSync | Works like a mouse | USB
LipSync Wireless | Works like a mouse | Wireless
LipSync Macro | Works like a keyboard | USB & wireless
LipSync Gaming | Works like a gaming joystick | USB

Wireless Status LED

Traps saliva
Sip-and-puff tubing

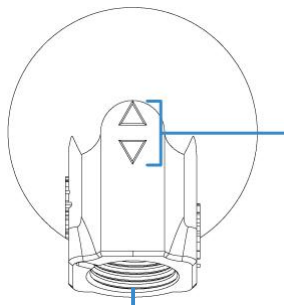
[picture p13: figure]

FRONT VIEW | FRONT VIEW | BACK VIEW

Speed buttons
Adjusts cursor speed

Mounting thread
5/8”

# 1 Getting Started

The LipSync requires the following items to get started:

- A LipSync
- Computing device (mobile phone, tablet, or laptop) which supports a USB mouse
- External power bank (optional but recommended)
- Mounting solution for securing the LipSync to a surface

Before plugging the LipSync, make sure of the following:

1. Computing device is fully charged and/or uses an external power source (e.g. power bank).
2. Computing device and LipSync are securely mounted to a stable surface.
3. LipSync USB, adapter cable and external power source are plugged together

### Mounting

Wheelchair: Every wheelchair has different points available for mounting. Common mounting points available on

power wheelchairs are the headrest rail, back of wheelchair, armrest rail, under chair cushion, chair rail, and

footplate. Try out different areas and see what works best. If you are not familiar with mounts, consult with an

assistive technology professional.

Desk: Find a clear space on the front edge of your desk or table. Orient the mount bracket toward the user being

careful not to move the LipSync. Secure the bracket and adjust the mounting arm so the LipSync is within easy

reach. Tighten the knob when the arm is in the desired position.

Checklist for after mounting:

☐ Are the clamp and mount secure and do not move?

☐ Is there clearance around the wheels, wires, and chair frame with the mount attached?

☐ Does the wheelchair fit through doorways?

☐ Is the driving view of the user clear with no obstructions?

☐ Is the mobile device within viewing angle of the LipSync?

☐ Can the user easily reach the LipSync to use it?

### Device Compatibility

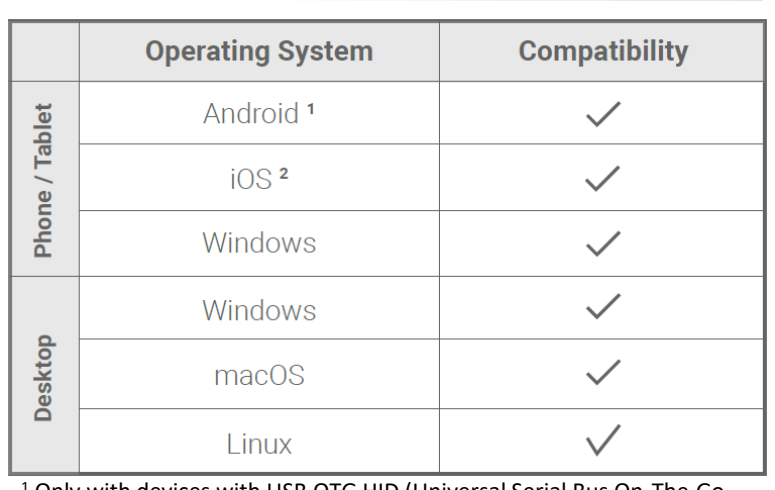
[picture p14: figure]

Not all mobile phones and tablets support external

pointing devices like the LipSync or other mouse

replacements. Apple iOS phones and tablets with

iOS13 and iPadOS or higher, and most Android and

Windows phones and tablets support the LipSync.

Check with the manufacturer before purchasing.

Look to see if your device supports “USB OTG HID”

or “Universal Serial Bus On the Go Human Interface

Device” profile.

### Powering the LipSync

The LipSync doesn’t have an internal battery so it needs to be powered at all times with an external power source.

Users can draw power off of the device (except on iOS devices) or use a power bank (>5000mAH) to prevent the

LipSync from drawing battery from device. While using a power bank, power is only supplied to the LipSync and the

mobile or tablet will not be charged.

1 Only with devices with USB OTG HID (Universal Serial Bus On-The-Go

Human Interfere Device)

2 Only for iOS13+ and iPadOS. For iOS12 and older, use the LipSync Macro

Device | USB adapter | Power bank

or

### Connecting the LipSync to a Device

Plugging into a Computer, Laptop or Android & Windows Device

The order in which you connect the USB cables may affect how the LipSync works. Connect the cables in the

following order:

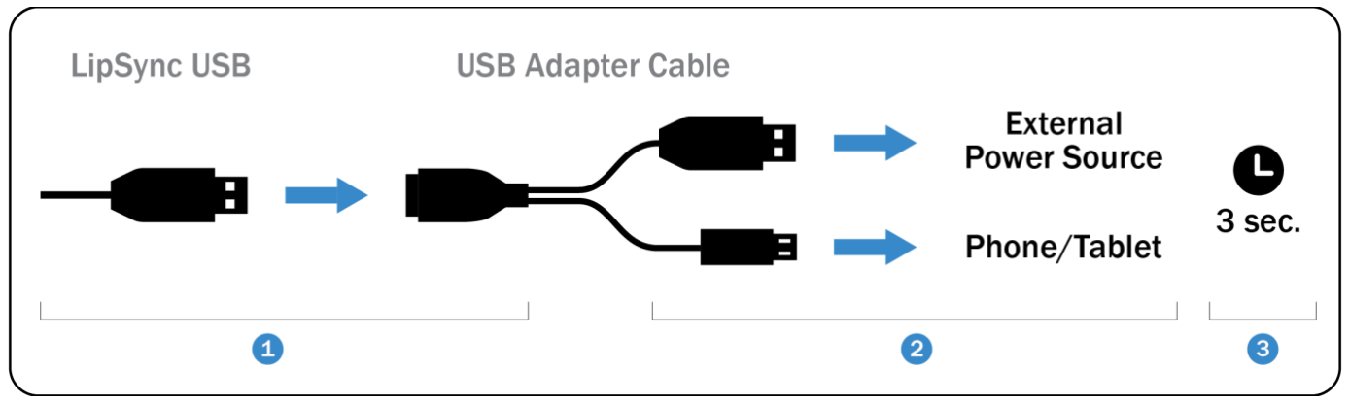
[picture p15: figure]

1. Connect the LipSync USB to the USB adapter cable’s receptacle.
2. Connect the other end of the adapter into the computing device and external power source.
3. Wait 3 seconds for the LipSync to initialize. Initialization is complete when the LED blinks red and green four

times.

Note: If you are using a desktop or laptop the LipSync USB can be directly plugged into the computer USB port.

Plugging into an iOS Device

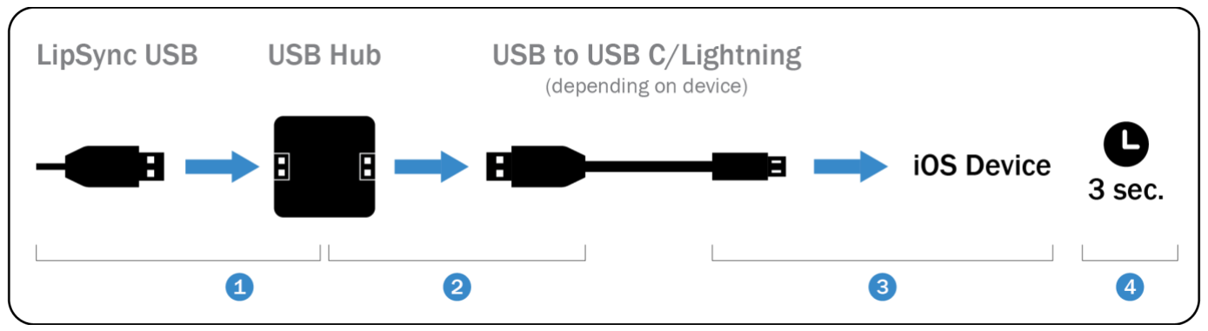
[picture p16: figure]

1. Connect the LipSync USB to a USB hub’s receptacle.
2. Connect the USB end of a USB to USB C/Lightning cable into the hub’s USB receptacle.
3. Connect the other end of the USB to USB C/Lightning cable into the iOS device.
4. Wait 3 seconds for the LipSync to initialize. Initialization is complete when the LED blinks red and green four

times.

### On-Screen Controls

The assistant menu is a floating onscreen menu that allows access to important functions that cannot be accessed

without physically touching the device, like the home button, back, zoom in and out, screen capture, volume, and

restart.

On Android devices, turn on the Assistant Menu by going to Setting → Accessibility → Dexterity and Interaction →

Assistant Menu

On iOS devices, turn on AssistiveTouch by going to Setting → Accessibility → Touch → AssistiveTouch

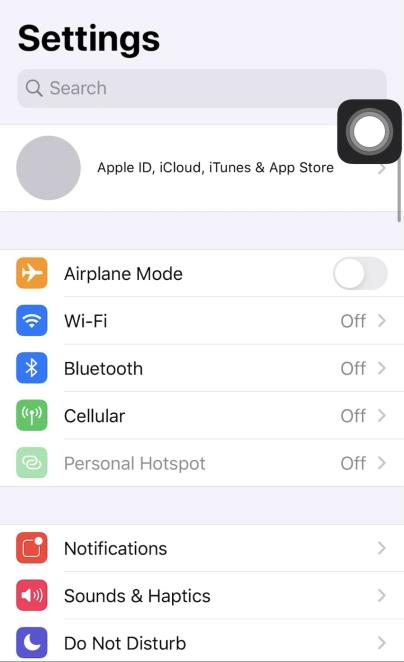
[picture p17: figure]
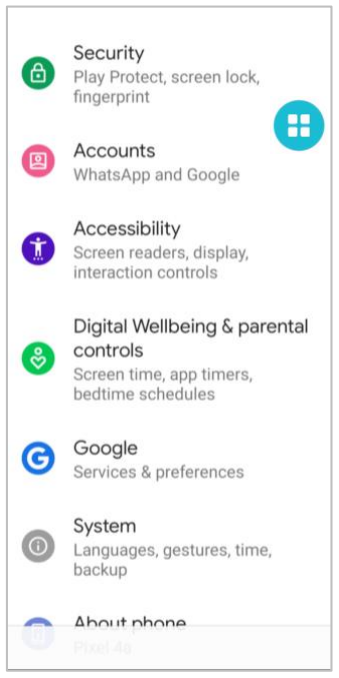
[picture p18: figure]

On some devices, a swiping action is required on some mobile device to unlock it. This can be avoided by setting

turning off screen lock. Alternatively, applications such as Keep Screen On can be downloaded from the Android

Play store to prevent the phone from going to sleep. However, this will drain your phone battery faster.

Android device | iOS device

# 2 Using the LipSync

IMPORTANT: Allow 3 seconds for the LipSync Status LED initialization sequence

to flash each time the LipSync is connected to a device wihtout moving the mouthpiece. Moving it

before the 3 seconds is complete will affect the usage

### Functions

FOR MOBILE DEVICES AND TABLETS

Function | Action | Time (seconds)
Tap | Puff | 1
Back button¹ | Sip | 1
Drag² | Puff | 3
Scrolling³ | Sip | 3
Cursor home reset | Puff | 5
No action | Sip | 5

1 The back/home functions may not work if the device uses on-screen icons. In this case, move

the cursor over the icon to tap.

2 The red LED will stay on at all times in this mode. Deactivate mode by doing a 1 second sip or puff.

3 The green LED will stay on at all times in this mode. Deactivate mode by doing a 1 second sip or puff.

Useful examples:

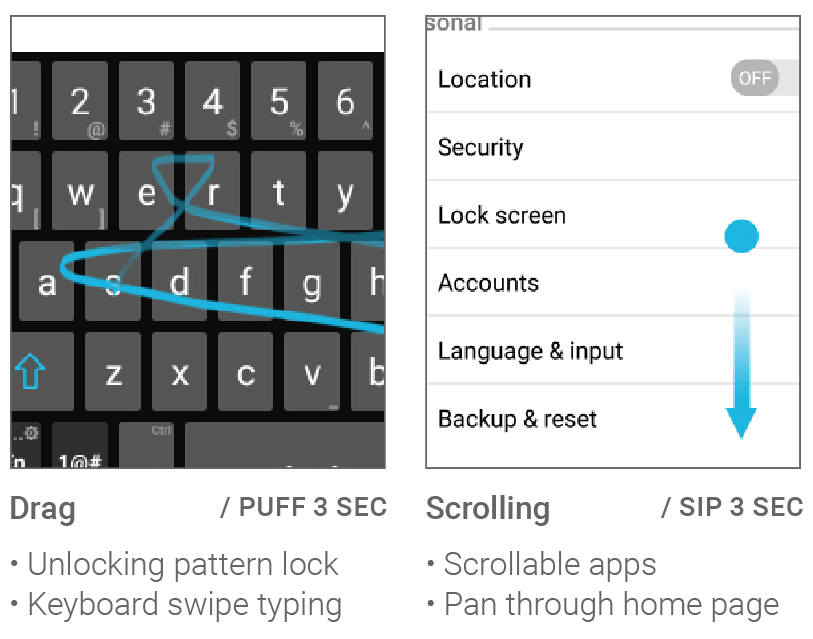
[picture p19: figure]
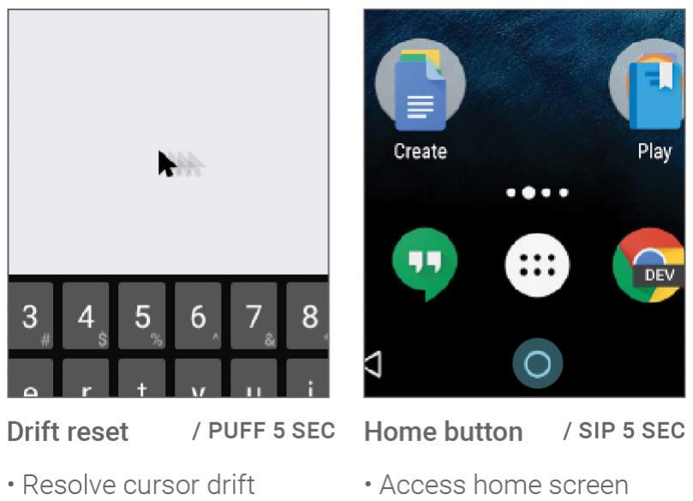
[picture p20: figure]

FOR PCs AND LAPTOPS

Function | Action | Time (seconds)
Left click | Puff | 1
Right click | Sip | 1
Double-click | Puff | 1 each
Drag¹ | Puff | 3
No action | Sip | 3
Cursor home reset | Puff | 5

1 The red LED will stay on at all times in this mode. Deactivate mode by doing a 1 second sip or puff.

Useful examples:

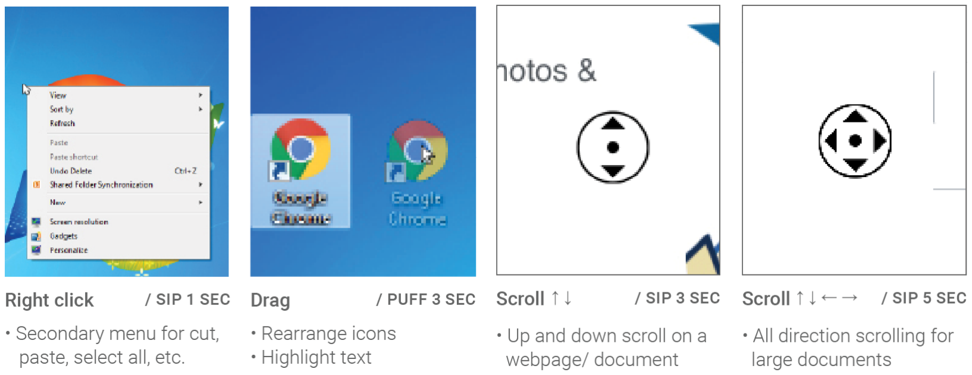
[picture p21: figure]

### Speed Control

The LipSync has 11 speed levels with the default level set to 5 when first set up. The

LipSync Status LED will blink the cursor speed level number.

Press the | button to increase the cursor speed
Press the | button to decrease the cursor speed.

To adjust the cursor sensitivity and speed, set the device’s cursor speed to its

slowest setting to start then adjust the LipSync speed control buttons. If it’s still not

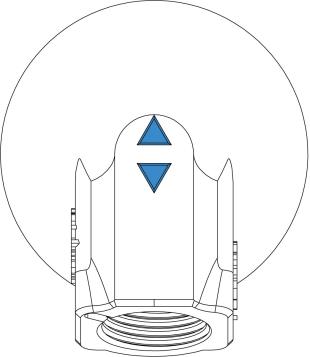
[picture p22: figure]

fast enough, gradually increase the speed on the device. | LipSync back view

# 3 Maintenance

### Cleaning the Mouthpiece and Filter

Each user should have their own set of mouthpiece and filter for hygienic reasons. These pieces are made of acrylic

plastic and have a 3-6 month life cycle depending on the usage. Keep unused pieces in a clean sealable bag out of

the sunlight.

Follow these steps to clean the pieces during its life cycle:

1. With the LipSync facing you and wearing clean gloves, twist the mouthpiece and filter counter clockwise to

detach it. If you’re having trouble removing the filter, see the next page.


2. To clean the mouthpiece: mix 1 cup (250 mL) of water with 2 tsp (10 mL) of 5% bleach (sodium

hypochlorite). Soak the mouthpiece for 10 minutes and then air dry or wipe with a clean cloth.

To clean the filter: throw away used filters that have trapped saliva and use a clean piece.

3. Wearing clean gloves, twist the mouthpiece and filter clockwise until finger tight. Do not overtighten.


Broken stem removal

If you’re unable to screw in a new LipSync air filter, it may be because a portion of the old filter has broken off and is

stuck inside the air fitting. To remove this broken piece, the best tool to use is a medical hemostat or very small vice

grips. You can also use fine nose needle nose pliers, however, you’ll need to be more careful with pliers so as not to

not to break the plastic and make the problem worse.

To remove using a hemostat: Insert one side of the hemostat tip into the middle of the broken off filter stem and

the other side of the tip to the outside of the protruding broken stem. Be extra careful not to grip on the outside of

the fitting that it’s in or you will damage the LipSync. Squeeze the handle on the hemostat until the teeth between

the finger holes lock. Finally, rotate the tip of the hemostat counter-clockwise to remove the broken stem.


If a hemostat is not available, use an extra fine tip needle nose pliers or vice but be even more careful as these

larger tools can damage the LipSync easily.

### Cleaning the LipSync Shell

✓ | Wipe with a non-abrasive cloth lightly dampen with water or cleaning alcohol
✗ | Don’t use abrasive cleaning materials.
✗ | Don’t soak the LipSync shell in any cleaning solutions

# 4 Troubleshooting

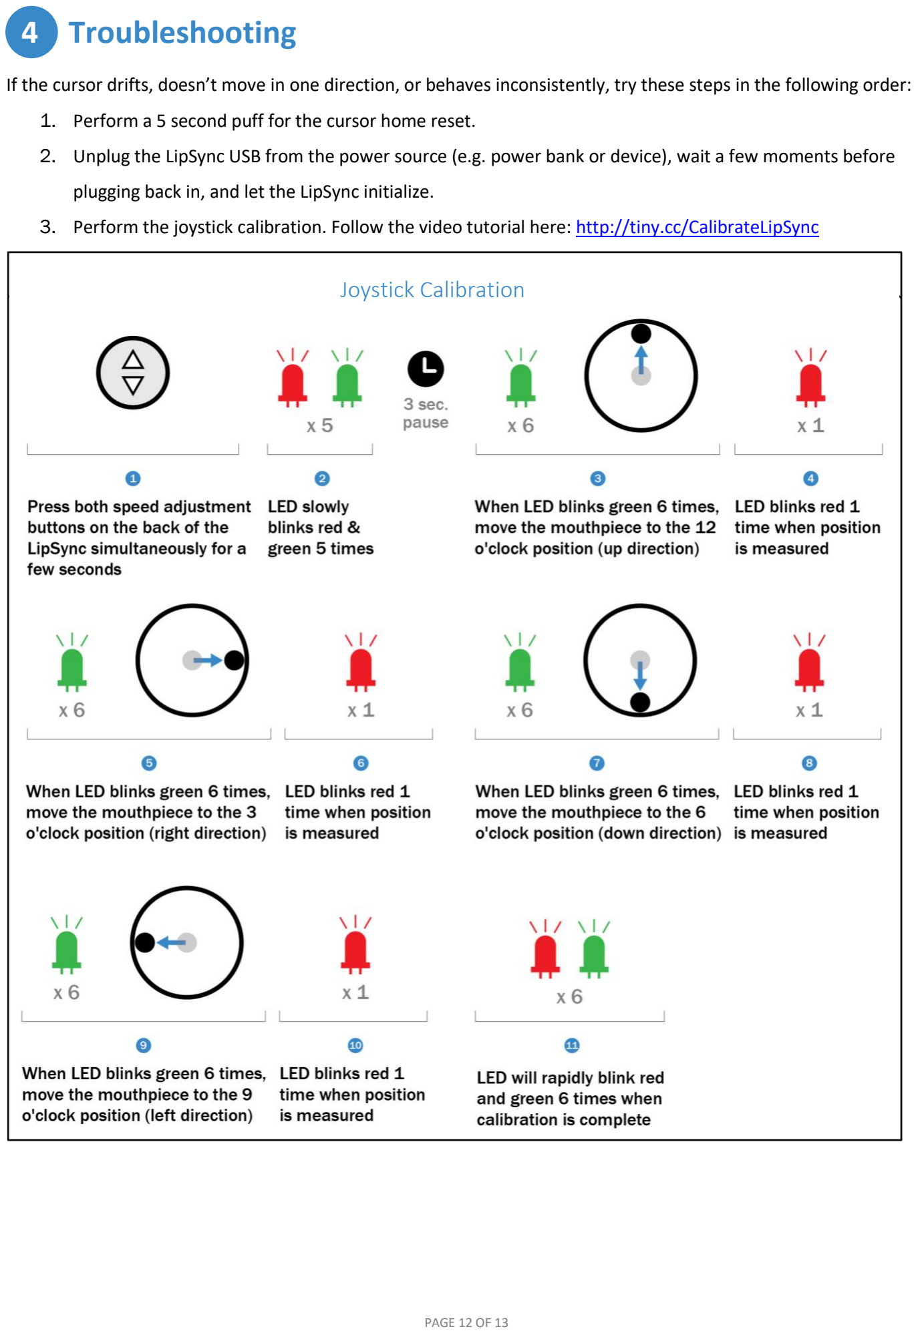
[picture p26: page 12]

If the cursor drifts, doesn’t move in one direction, or behaves inconsistently, try these steps in the following order:

1. Perform a 5 second puff for the cursor home reset.
2. Unplug the LipSync USB from the power source (e.g. power bank or device), wait a few moments before

plugging back in, and let the LipSync initialize.

3. Perform the joystick calibration. Follow the video tutorial here: http://tiny.cc/CalibrateLipSync

### Joystick Calibration

# 5 Feedback

The LipSync is an open-source project, which means that anyone and everyone is able to build the device and

improve upon the design. If you have suggestions for how to improve the LipSync or require technical help, please

reach out using one of the following routes:

1. Contact your LipSync maker
2. Makers Making Change Forum (https://makersmakingchange.com/forum/)
3. Leave a review on the LipSync page (https://www.makersmakingchange.com/project/lipsync/)

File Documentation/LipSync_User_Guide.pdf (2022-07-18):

Version 1.3 | June 2022
PAGE 1 OF 2 | www.MakersMakingChange.com

or

# LipSync: User Guide

## Introduction

The LipSync is a sip-and-puff joystick that allows a user with limited or no arm mobility to control their computer with their mouth. It emulates a computer mouse and can perform left and right clicks, scroll, and other mouse actions.

This assistive device is suitable for users with spinal cord injury, MS, ALS, and other disabilities that restrict arm movement.

## Device Compatibility

## Parts of the LipSync

## Powering the LipSync

The LipSync doesn’t have an internal battery so it needs to be powered at all times with an external power source. Users can draw power off of the device (except on iOS devices) or use a power bank.

## Initialization

Allow 3 seconds for the LipSync to initialize and set the home position every time the LipSync is connected to power. The LipSync Status LED will flash 6 times,
alternating between red and green | .
Wait until the LED stops flashing before moving the mouthpiece.

## Connecting to a Device

For computers and Android & Windows devices connect the LipSync USB into the device. Use an adapter if necessary.

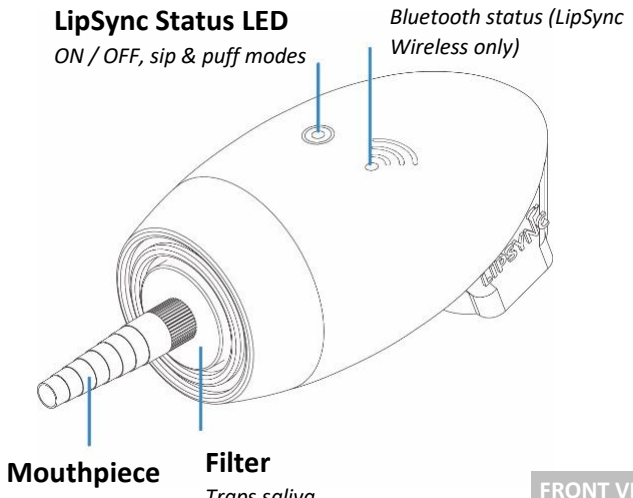
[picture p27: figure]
LipSync Status LED; ON / OFF, sip & puff modes; Bluetooth status (LipSync Wireless only); Filter; Mouthpiece

For iOS devices connect the LipSync USB into a USB hub. Use a USB to USB C/Lightning (depending on the device used) to connect the USB hub to your device.

## Cursor Setup on iOS Devices

1. Open your device’s Settings > Accessibility > Touch > AssistiveTouch > Turn it on.
2. Turn off Always Show Menu

Phone
Android 4.0+
iOS13+
Windows

Device

Tablet
Android 4.0+
iPadOS+
Windows

Power bank
(>5000 mAh)

USB
adapter

Speed buttons
Adjusts cursor speed

Wireless Status LED

Traps saliva
Sip-and-puff tubing

Computer & Laptop
Windows
MacOS

FRONT VIEW

BACK VIEW

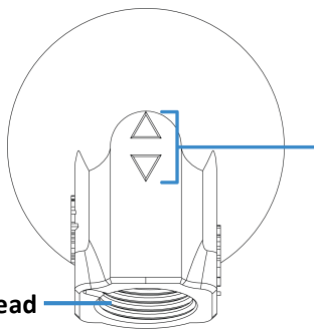
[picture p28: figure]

Mounting thread
5/8”

Version 1.3 | June 2022

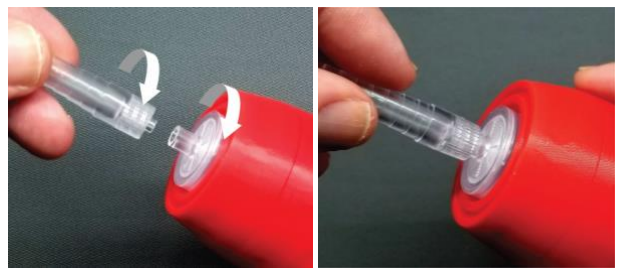
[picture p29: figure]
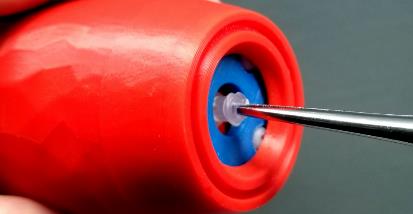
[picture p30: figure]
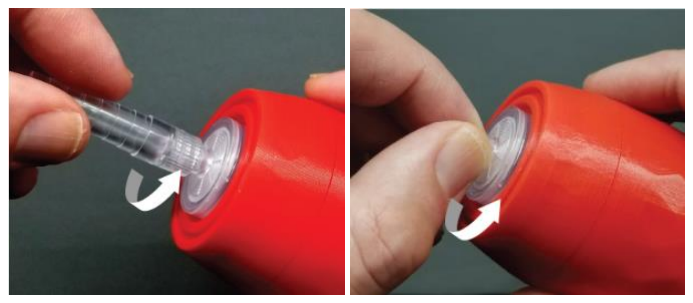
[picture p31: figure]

PAGE 2 OF 2 | www.MakersMakingChange.com
1 | 2 | 3 | 4 | 5 | 6 | 7 | 8 | 9 | 10 | 11

## Functions for Mobile or Tablet

1 If the device uses on-screen icons, move the cursor over the icon to tap.
2 The red LED will stay on at all times in this mode. Deactivate by doing a 1 second sip or puff.
3 The green LED will stay on at all times in this mode. Deactivate by doing a 1 second sip or puff.

## Functions for Computer

FUNCTION | ACTION | ACTION TIME (SECONDS)
Left click | Puff | 1
Right click | Sip | 1
Double-click | Puff | 1 each
Drag² | Puff | 3
Scrolling³ | Sip | 3
Cursor home reset | Puff | 5
No action | Sip | 5

## Cursor Speed Control

Press the | button to increase the cursor speed.
Press the | button to decrease the cursor speed.

The LipSync Status LED will blink the cursor speed level number. The previous speed setting will be saved the next time the LipSync is used.

## Cleaning the Mouthpiece and Filter

Each user should have their own set of mouthpiece and filter for hygienic reasons. These pieces are made of acrylic plastic and have a 3–6-month life cycle.

1. With the LipSync facing you and wearing clean gloves, twist the mouthpiece and filter counter clockwise to remove them.
2. If the filter doesn’t twist off or the filter stem is broken, use a hemostat or extra fine tip needle nose pliers to grip and carefully twist it off. See the LipSync: Startup Guide for in-depth instructions.
3. To clean the mouthpiece: mix 1 cup (250 mL) of water with 2 tsp (10 mL) of 5% bleach (sodium hypochlorite). Soak it for 10 minutes and let it air dry or wipe with clean cloth.
To clean the filter: throw away used filters that have trapped saliva and use a clean piece.
4. Wearing clean gloves, twist the mouthpiece and filter clockwise until finger tight. Do not overtighten.

## Cleaning the LipSync Shell

✓ | Wipe with a non-abrasive cloth lightly dampen with
| water or cleaning alcohol
✗ | Don’t use abrasive cleaning materials
✗ | Don’t soak the LipSync shell in any cleaning solutions

## Troubleshooting Cursor Issues

If users encounter drifting or inconsistent cursor

movement, follow these steps in order: http://tiny.cc/CalibrateLipSync

1. Perform a 5 second puff for the cursor home reset.
2. Unplug the LipSync USB from the power source (e.g. power bank or device), wait a few moments before plugging it back, and let the LipSync initialize.
3. Perform joystick calibration. See the last page on the LipSync: Startup Guide or watch the calibration tutorial on YouTube (https://tiny.cc/CalibrateLipSync).

If steps 1-3 doesn’t resolve the cursor issue, contact your LipSync maker or go to the Makers Making Change Forum (https://forum.MakersMakingChange.com) for assistance.

FUNCTION | ACTION | ACTION TIME (SECONDS)
Tap | Puff | 1
Back button¹ | Sip | 1
Drag² | Puff | 3
Scrolling³ | Sip | 3
Cursor home reset | Puff | 5
No action | Sip | 5
Slowest | Default level | Fastest

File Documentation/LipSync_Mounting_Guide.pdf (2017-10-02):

# MOUNTING THE LIPSYNC

## By: Manal Faour

## Contents

Introduction The LipSync is a mouth operated mouse replacement that allows people with severe mobility

impairments to use mobile devices such as a mobile phone. The lightness of the LipSync as well as its compactness make it a great candidate for portable, wheelchair mounted applications but some considerations need to be taken when choosing a mounting option to ensure ease of use and safety of the user. This document details the considerations of how to mount the LipSync. Now that you have the LipSync, how can you mount it onto a wheelchair? What options are there for your mobile device? What are some of the considerations to have in mind when choosing a mounting option?

## Mounting to a Wheelchair

## Mounting Points

Every wheelchair is different in terms of the points available for mounting. Below is a list of some common mounting points that are available on power wheelchairs. The sketches illustrate the locations of these mounting points on the wheelchair.
1. Headrest rail
2. Back of wheelchair
3. Armrest rail
4. Under chair cushion
5. Chair rail
6. Footplate


Side View - Headrest

Side View - Armrest

Back View - Wheelchair

Side View - Chair Cushion and Rail

Side View - Footplate

Figure 1 - Sketch of Power Wheelchair and Views of its Components

## Considerations

When choosing a mount, many things need to be taken into consideration to ensure the safety of the user. Below you'll find a complete detailed list of these considerations. For a quick checklist, refer to Appendix A Checklist for After Choosing a Mount.
1. Mounting at the sides can make doorways difficult to navigate. Modern wheelchairs are 24"-27" in width and a wheelchair accessible door is usually 32" therefore care should be taken when mounting to the side of the wheelchair. Ensure that the addition of the mount at the sides of the wheelchair does not extend beyond the wheelchair frame to avoid hitting the doorway and potentially dislodging the mount, thereby putting the user at a safety risk. There is also a risk of the mount getting caught in obstacles. The image below demonstrates a setup that must be avoided as it can be easily snagged on something or could potentially bump into surrounding objects.

Knob protruding past wheelchair wheel

Figure 2 - Image of an Unacceptable Mount Setup
2. Attaching a clamp vertically may cause slipping of the mount. Therefore care must be taken when mounting in this direction.
3. To increase the friction and avoid slipping of a clamp additional anti skid pads may be added. A common product that is used for this purpose is Dycem, which provides reels of non-slip mats and tapes. Another option is "Magic Wrap" used for plumbing repairs.
4. Care should be taken when mounting to the headrest especially in reclining chairs. In a reclined position, the mount is more likely to detach and fall. Some solutions to this problem is increasing the friction of the mount using methods described above. Another solution is to choose a mount that completely encases the rail of the headrest as shown in the image below.


Figure 3 - A bottom and isometric view of a clamp that does not encase the rail vs. one that does
5. Wiring must be avoided to prevent faulty connections of the wheelchair devices.
6. Clearance around the wheels must be maintained to avoid detachment of the device or damage to the wheelchair.
7. In many wheelchairs, reclining causes a few components of the wheelchair to shift in position. Therefore, when choosing a mounting point check that there is clearance around the different components in both a reclined and non-reclined position.
8. When positioning the LipSync, care should be taken to ensure that the driving view of the user is not obstructed.
9. When positioning the LipSync, make sure that it is vertically aligned as described in Figure 4. Assemblies with goosenecks or ball and sockets at the top allow for positioning the LipSync vertically.


Figure 4 - Left: LipSync Positioned Vertically; Right: LipSync Positioned Non-vertically
10. When positioning the mobile device ensure that it is within viewing angle of the LipSync. The normal optical axis for a person in a sitting position is at 15° below eye level (Figure 4).
For example, if mounting a phone 35cm away from your face, the normal optical axis for a person in a sitting position is 15° below the 0° line, which translates to 7cm below eye level at that distance (Appendix D Field of Vision Claculations). The Limit of the range of vision is at 70-80°.


Figure 5 - Field of Vision Range ((SOLIDERE) & (ESCWA), 1994)
11. When positioning the mobile device, make sure that it is adjusted to avoid glare from the sun. In some cases, it may be necessary to add an anti-glare screen protector to the mobile device available here. (https://www.amazon.ca/Tech-Armor-Anti-Glare-Anti-Fingerprint-Protectors/dp/B00IGISQUO)
12. On some power wheelchairs, the armrest can be lifted to allow for transferring the wheelchair user. Therefore, mounting to that side of the wheelchair in those cases is not recommended.
13. Mounting at the back of the wheelchair requires the mount to be very long compared to other mounting points. In this position the mount experiences a large amount of torque which could cause it to fail.

Suppliers The following list is meant to serve as an introduction to suppliers that offer mounts that could be used

for the LipSync or a mobile device. The list is by no means exclusive since many other retailers sell mounts that work for our application either specific to assistive technology or not.

## On-Stage

https://on-stage.com/
On-Stage manufactures a range of stands for musical instruments and microphones. Advantages
a. It offers solutions at a lower price in comparison to the other suppliers.

Drawbacks
b. The goosenecks they offer are used for light weights and may sag under a heavy weight.
Sample Parts and Approximate Prices
Part No. | Description | Supplier | Qty | Approximate Cost (CAD)
MSA9030-19B | 19" Gooseneck, Black | Best Buy | 1 | $15
MSA9030-13B | 13" Gooseneck, Black | Best Buy | 1 | $10
MSA9030-06B | 6" Gooseneck, Black | Best Buy | 1 | $7
MSA9505 | Posi-Lock Telescoping Mini-Boom | Best Buy | 1 | $30

## Loc Line

http://www.loc-line.com/
Lockwood products inc manufactures Loc-Line - a range of adjustable plastic hoses and adaptors originally developed for cooling purposes in machine tool operations.
Advantages
a. Hand adjustable for both position and length.
b. Unique ball and socket design, bending does not decrease the inside diameter.
c. Can be twisted along its axis.
d. Easily washable and is resistant to most common chemicals.
e. Reasonably priced and is widely available.
f. Hollow so a wire can be fed through it.
g. Able to use for both the phone and the LipSync device using one setup (Y fitting). Drawbacks
a. Not suitable for applications where high loads are involved.
Sample Parts and Approximate Prices
* EH Pope is a Canadian distributor
Part No. | Description | Supplier | Qty | Approximate Cost (CAD)
Direct Mounting Solutions (to wheelchair)
510001 | Spring Clamp, 2", with integrated 3/4" ID Fixed Mount. Assembled. | Modular Hose | 1 | $9
512001 | Round Tube and Flat Surface Clamp Kit. | Modular Hose | 1 | $39
Extension Lines
61501 | Hose Segments Pack for 3/4" ID System. Includes (2) 5" long segments. Approximately 1 foot. | EH Pope | 1 | $7
51801 | Hose Segments Pack for 1/2" ID System. Includes (2) 5" long segments. Approximately 1 foot. | EH Pope | 1 | $6

## Ablenet

https://www.ablenetinc.com/technology/mounting-cases
Advantages
a. The mounts are all sold as a whole piece - no need to buy anything else.
b. Many available options from a gooseneck to mounting arms. Drawbacks
a. Relatively expensive.
Sample Parts and Approximate Prices
Part No. | Description | Supplier | Qty | Approximate Cost (CAD)
- | Latitude Mounting Arm (quick release) | Ablenet | 1 | $440
- | Gooseneck Mounting System | Ablenet | 1 | $250
- | Friction Knob Universal Mounting System | Ablenet | 1 | $325

## SnakeClamp

http://snakeclamp.com/Category/smartphone-snakeclamp-desk-stand-mount-holder-flexible-goosneck-arm (http://snakeclamp.com/Category/smartphone-snakeclamp-desk-stand-mount-holder-flexible-goosneck-arm)
Advantages
a. You have the option of building your own mount.
b. Heavy duty goosenecks are available.
Drawbacks
a. Goosenecks may be unstable and sag under heavy weight.
Sample Parts and Approximate Prices
Part No. | Description | Supplier | Qty | Approximate Cost (CAD)
Direct Mounting Solutions (to wheelchair)
SCP-MC | Multiclamp | SnakeClamp | 1 | $39
Extension Lines
SCP-GN24 | 24" Heavy Duty Flexible Gooseneck Arm | SnakeClamp | 1 | $39
SCP-GN18 | 18" Flexible Gooseneck Arm | SnakeClamp | 1 | $22
SCP-GN18HD | 18" Heavy-Duty Flexible Gooseneck Arm | SnakeClamp | 1 | $24
SCP-GN13B | 13" Flexible Gooseneck Arm, Black | SnakeClamp | 1 | $22
SCP-GN09 | 9" Flexible Gooseneck Arm | SnakeClamp | 1 | $14
SCP-RA12 | 12" Rigid Arm | SnakeClamp | 1 | $18

## Manfrotto

https://www.manfrotto.ca/
Manfrotto manufactures a range of clamps, adaptors and fixtures for mounting cameras, lighting devices and studio accessories.
Advantages
a. Load carrying capacity is relatively high.
Drawbacks
a. Cost is relatively high.
b. Electrically conductive.
c. Heavy, bulky and has a very 'industrial' appearance. Sample Parts and Approximate Prices
Part No. | Description | Load
capacity
(kg)

Max length
(mm)
Supplier | Qty | Approximate
Price (CAD)
Direct Mounting Solutions (to wheelchair)
171 | Mini clamp | 1 | - | Manfrotto | 1 | $40
035 | Super Clamp | 15 | - | Manfrotto | 1 | $57
635 | Quick Action Super Clamp | 15 | - | Manfrotto | 1 | $70
Extension Lines
244N | Variable friction arm | 3 | 530 | Manfrotto | 1 | $200
237 | Flex arm. ID 13mm. | 0.3 | 550 | Manfrotto | 1 | $50
237 HD | Heavy duty flex arm. ID 18mm. | 0.5 | 550 | Manfrotto | 1 | $60
196AB-2 | Single articulated arm: 2 sections | 1.5 | 605 | Manfrotto | 1 | $55

## LinkDelight

http://linkdelight.com/en/.html
LinkDelight offers a range of photography equipment. Advantages
a. Offers compact and small mounts.
Drawbacks
a. Mainly aimed at the photography industry therefore some adapters need to be purchased. Sample Parts and Approximate Prices
Part No. | Description | Supplier | Qty | Approximate Cost (CAD)
| 11" Magic Adjustable Arm for Lilliput Monitor / | Amazon | 1 | $15

LED Light Video Monitor
11" Articulating Magic Arm + Small Clamp Crab Pliers + Gopro Adapter+ Stainless Steel Thumber Screw Accessory Kit | LinkDelight | 1 | $24
Digital Camera Camcorder Mini Ballhead 1/4" Screw Thread Base | LinkDelight | 1 | $6
Mini Ball Head with Lock and Hot Shoe Adapter Camera | Amazon | 1 | $5

## Mobility Mount

http://www.mobilitymount.com/
Mobility Mount provides mounts specifically for wheelchair users. It's uniqueness lies in the fact that the base of the mount is held under the seat cushion. Many adapters are available to allow for mounting multiple devices.
Advantages
a. Mount sits under chair cushion therefore no mounting points necessary.
Disadvantages
a. Expensive to buy.
Sample Parts and Approximate Prices
Part No. | Description | Supplier | Qty | Approximate Cost (CAD)
MM01 | Base with tube | Mobility Mount | 1 | $320
MT | Multi Table 10X14 with no slip | Mobility Mount | 1 | $155
TC | Tablet Configuration for table | Mobility Mount | 1 | $115

Mounting Assemblies Below you'll find some wheelchair mounting options for the LipSync, a mobile device, or the

combination of both. Endless setups may be assembled to fit a the user's needs. Some setups may be more convenient than others depending on the considerations listed in the previous sections. Some of these components can be purchased from other suppliers.

## LipSync

The LipSync has a standard 5/8"-27 thread female connection. The mounting options below include a 5/8"-27 thread male connection in order to connect to the LipSync.

### Mounting Options Per Price Range

$0 - $49
Most of the options below include a 3D printed clamp which contributes to the reduced price. The downside of using 3D printed parts is the reduction in the strength of the component and the likelihood of it breaking if used to hold up a heavy weight.
For the assembly instructions of the 3D Printed Clamp refer to Appendix B Assembly Instructions for 3D Printed Clamp.
For assembly instruction of the DIY Mount refer to Appendix C Assembly Instructions for DIY Mount. Note: There are two possible assemblies for the DIY Mount. A Mini Ball Head with Lock may be used in cases where the articulating arm and the arrow shafts do not provide enough flexibility to position the LipSync vertically. Steps for both options are included below.
Part No. | Description | Qty | Supplier | Approximate Cost (CAD)

Total
Option 1 - DIY Mount
3D Printed Clamp + Nuts and Bolts | 1 | - | $3 | $3
Female 1/4"-20 to 5/8"-27 Male 2 Piece Mic Adapter | 1 | Amazon | $9 | $9
11" Inch Friction Articulating Magic Arm for Camera DSLR | 1 | Amazon | $14 | $14
3D Printed 1/4-20 threaded insert | 1 | - | $0 | $0
Arrow shaft | 1 | Local Archery Store/Walmart | $7 | $7
3D printed Disk Gear + Nut and Bolt | 1 | - | $2 | $2
3D Printed 3/8-16 threaded holder | 1 | - | $0 | $0
For the second possible assembly
Mini Ball Head with Lock and Hot Shoe Adapter Camera | 1 | Amazon | $5 | $5
1/4 male to 3/8 male adapter | 1 | Amazon | $7 | $7
3/8 female to 5/8 male adapter | 1 | Amazon | $7 | $7
| | | TOTAL | $35 (Or $54)


Figure 6 - From Left to Right: 3D Printed Clamp, Adapter, Articulating Arm, 3D Printed Adapter, Arrow Shaft, Disk Gear & Hand Knob, Arrow Shaft, 3D Printed Adapter, LipSync
Option 2
3D Printed Clamp + Nuts and Bolts | 1 | - | $3 | $3 1/4" Male To 3/8" Male Thread
| Adapter | 1 | Amazon | $7 | $7
| 3/8" Female to 5/8" Male thread adapter | 1 | Amazon | $7 | $7
MSA9030-19B | 19" Gooseneck, Black | 1 | Best Buy | $15 | $15
MSA9030-13B | 13" Gooseneck, Black | 1 | Best Buy | $10 | $10
| | | | TOTAL | $43


Figure 7 - From Left to Right: 3D Printed Clamp, Adapters, 19" Gooseneck, 13" Gooseneck, LipSync
Option 3
11" Articulating Magic Arm + Small Clamp Crab Pliers + Gopro Adapter+ Stainless Steel Thumber Screw Accessory Kit | 1 | Link Delight | $24 | $24
Female 1/4"-20 to 5/8"-27 Male 2 Piece Mic Adapter | 1 | Amazon | $9 | $9
19" Gooseneck, Black | 1 | Best Buy | $15 | $15
| | | TOTAL | $48
$50-$99
The options below increase in price due to the use of a commercial clamp (with the exception of option 2). The price is still otherwise competitive compared to other options due to the fact that the parts used are not necessarily meant for assistive technology applications. For instance as mentioned in the previous section (Suppliers), Loc Line was originally developed for cooling purposes for machine tool operations.
Part No. | Description | Qty | Supplier | Approximate Cost (CAD)

Total
Option 1
| Clamp with standard stud | 1 | Amazon | $28 | $28
MSA9030-19B | 19" Gooseneck, Black | 1 | Best Buy | $15 | $15
MSA9030-13B | 13" Gooseneck, Black | 1 | Best Buy | $10 | $10
| | | | TOTAL | $53


Figure 8 - From left to right: Super Clamp, Standard Stud, 19" Gooseneck, 13" Gooseneck, LipSync
Option 2
| 3D Printed Clamp+Nuts and Bolts | 1 | - | $3 | $3
| 1/4" Male To 3/8" Male Thread Adapter | 1 | Amazon | $7 | $7
| 3/8" Female to 5/8" Male thread adapter | 1 | Amazon | $7 | $7
MSA9505 | Posi-Lock Telescoping Mini-Boom | 1 | Amazon | $30 | $30
MSA9030-19B | 6" Gooseneck, Black | 1 | Best Buy | $7 | $7
| | | | TOTAL | $54


Figure 9 - From Left to Right: 3D Printed Clamp, Adapters, Posi-Lock Telescoping Mini-Boom, 13" Gooseneck, LipSync

Option 3
512001 | Round Tube and Flat Surface Clamp Kit. (see above) | 1 | Modular Hose | $39 | $39
61501 | Loc-Line Hose Segments Pack for 3/4" ID System. Includes (2) 5 3/4" segments. Approximately 1 foot. (see above) | 1 | EH Pope | $7 | $7
51801 | 1/2" Hose, one foot, in Black (51801-BLK) -1/2" Black Loc-Line | 1 | EH Pope | $6 | $6
61508 | 3/4" to 1/2" Adapter in Black (61508-BLK) -Black Hose | 1 | EH Pope | $3 | $3
51805 | 1/2" NPT Connector in Black (51805-BLK) -1/2" Black Loc-Line | 1 | EH Pope | $1 | $1
| | | | TOTAL | $56

Option 4
| Clamp with standard stud | 1 | | $28 | $28
MSA9505 | Posi-Lock Telescoping Mini-Boom | 1 | Amazon | $29 | $29
MSA9030-19B | 13" Gooseneck, Black | 1 | Best Buy | $10 | $10
| | | | TOTAL | $67

$100+
These assemblies are used in industries such as the assistive technology industry or the photography industry. Their robustness, weight capacity and industrial use drive their prices up.
Part No. | Description | Qty | Supplier | Approximate Cost (CAD)

Total
Option 1
035 | Super Clamp | 1 | Manfrot to | $57 | $57
237 HD | Heavy duty flex arm. ID 18mm. | 1 | Manfrot to | $50 | $50
| Female 1/4"-20 to 5/8"-27 Female Adapter | 1 | Amazon | $9 | $9
| | | | TOTAL | $116

Option 2
| Clamp with standard stud | 1 | Amazon | $28 | $28
244N | Variable friction arm | 1 | Manfrot to | $210 | $200
| 1/4" To 3/8" Thread Adapter | 1 | Amazon | $9 | $9
| 5/8" Male to 3/8" Female Microphone Mic Stand Adapter | 1 | Amazon | $3 | $3
| | | | TOTAL | $240

## Mobile Device

No Mount
In many cases, the mobile device may be placed on the users lap, the lap tray mounted on their wheelchair, or on a table in front of the user. In this case there is no need for a mount. A stand may be used to adjust the viewing angle of the phone.
Mount
Phone mounts have a standard 1/4"-20 female thread. Therefore any mobile device holder may be selected in combination with the LipSync mounting options listed in the previous section (LipSync). The changes that need to be made relate to adding an adapter with a 1/4"-20 male thread. One potential option for a phone mount assembly is listed in the table below.
Part No. | Description | Qty | Supplier | Approximate Cost (CAD) | Total
| Mudder Universal Smartphone Holder Mount Adapter for Monopod Tripod Selfie Stick with Double Screw Head, Black | 1 | Amazon | $13 | $13
| Thread Adapter Microphone Stand 5/8"-27 Female to 1/4"-20 Male for Camera Monitor | 1 | Amazon | $9 | $9
MSA9030-19B | 19" Gooseneck, Black | 1 | Best Buy | $15 | $15
| Clamp with standard stud | 1 | Amazon | $28 | $28
| | | | TOTAL | $65

Combining LipSync and Mobile Device
There are some options to combine both the LipSync and a mobile device into one mount assembly setup. The idea of combining the LipSync and a mobile device simplifies the mount assembly process since it requires choosing only one mounting point. Combining the two systems also allows for a reduction in price since only one clamp is used. Two possible combinations were assessed and will be detailed below.
The first option includes the Loc Line hoses. Since a Y fitting is available, a system using these hoses can be formed to attach both a mobile device and the LipSync. The table below provides a complete assembly.
Part No. | Description | Qty | Supplier | Approximate Cost (CAD) | Total
512001 | Round Tube and Flat Surface Clamp Kit. | 1 | Modular Hose | $39 | $39
61501 | Loc-Line Hose Segments Pack for 3/4" ID System. Includes (2) 5 3/4" segments. Approximately 1 foot. (see above) | 2 | EH Pope | $7 | $14
51801 | 1/2" Hose, one foot, in Black (51801-BLK) -1/2" Black Loc-Line | 1 | EH Pope | $6 | $6
61511 | Loc-Line Y Fitting for 3/4" ID System. | 2 | EH Pope | $4 | $4
61508 | 3/4" to 1/2" Adapter in Black (61508-BLK) -Black Hose | 1 | EH Pope | $3 | $3

570009 | Extra deep V-tabs for tabX tablet holder. | 1 | Modular Hose | $24 | $24
51805 | 1/2" NPT Connector in Black (51805-BLK) -1/2" Black Loc-Line | 1 | EH Pope | $1 | $1
| | | | TOTAL | $91

The second option was developed for using goosenecks. This option includes a 3D printed bracket with 2 holes for the goosenecks. The image below shows the bracket holding 1 gooseneck. The other hole is meant to support another gooseneck


Figure 10 - 3D Printed Bracket Holding a Gooseneck
Part No. | Description | Qty | Supplier | Approximate Cost (CAD) | Total
| Clamp with standard stud | 1 | Amazon | $28 | $28
| 3D printed bracket | 1 | | $3 | $3
MSA9030-19B | 19" Gooseneck, Black 13" Gooseneck, Black | 2 1 | Best Buy Best Buy | $15 $10 | $30 MSA9030-13B $10 TOTAL $71

## Suggestions for Assembling Mounts

1. Tape some anti-skid pads like Dycem pads or "Magic Wrap" to increase the friction of the clamps and reduce their rotation about the tube.
2. If two assembly pieces are used, such as two goosenecks, glue them together at the attachment point to avoid separation or rotation.
3. Some of the problems associated with Loc-Line and goosenecks is the instability and their tendency to sag after continuous use. This could be solved using rescue tape, electrical tape or "Magic Wrap" wrapped around the pieces. Another solution is to add a stiff wire to the inside of the parts.
4. Goosenecks are a good option for small sections, but may become unstable as the length increases and may sag under their own weight. Therefore, it is not advisable to use goosenecks when the mounting point is further away from the user, such as the back of the wheelchair.
5. When using Loc Line, use the 3/4" tubes as the base to provide stability and stiffness to the setup. 1/2" tubes may be used at the top of the assembly.

### Appendix A Checklist for After Choosing a Mount

☐ Is the clamp secure and does not move?
☐ With the mount attached is there clearance around the wheels/wires/chair frame? ☐ Does the wheelchair fit through doorways?
☐ Is it possible for the mount to be snagged on obstructions as the user drives around? ☐ Is the driving view of the user clear with no obstructions?
☐ Is the mobile device within viewing angle of the LipSync?
☐ Can the user easily reach the LipSync to use it?

### Appendix B Assembly Instructions for 3D Printed Clamp

Tools:
1. Screwdriver
2. Glue
Components:
1. (4) 6-32x1" Round Head Machine Screws
2. (4) 6-32 Hex Machine Nuts
3. 3D Printed Clamp
4. 2" Piece of Magic Wrap
5. (1) Female 1/4"-20 to 5/8"-27 Male 2 Piece Mic Adapter
Steps:
1. Glue the 4 nuts in their assigned slots on the bottom piece of the clamp. Make sure not to add too much glue to avoid blocking the hole.


Figure 11 - Glued Nuts in Bottom Piece of Clamp
2. Glue the Female 1/4"-20 to 5/8"-27 Male 2 Piece Mic Adapter into the hole in the assembled 3D printed clamp as shown in the image below.


Figure 12 - Glued 1/4"-20 to 5/8"-27 Adapter in 3D Printed Clamp
3. Wrap the 2" piece of Magic Wrap around the section of the tube that you plan on mounting in to.


Figure 13 - Magic Wrap Around Wheelchair Tube
4. Place the bottom piece of the clamp on the Magic Wrap.
5. Align the top piece with the bottom piece and screw in the first bolt until it is secure. Repeat for the other 3 bolts.


Figure 14 - Complete Assembly of Clamp

### Appendix C Assembly Instructions for DIY Mount

Tools:
1. Glue
2. Tube Cutter or Saw
Components:
1. (1) 5/16 in.-24 tpi x 1-1/2 in. Hex Cap Screw
2. (1) 5/16 in. Nut
3. 3D Printed Clamp
4. 3D Printed Disk Gear & Hand Knob
5. 3D Printed Threaded Adapters: 1/4-20 threaded insert & 3/8-16 threaded holder
6. 11" Inch Friction Articulating Magic Arm for Camera DSLR
7. Arrow Shaft - for the models provided we used an Easton Eclipse 2512 Arrow Shaft For the second possible assembly:
8. Mini Ball Head with Lock and Hot Shoe Adapter Camera (optional)
9. 1/4 male to 3/8 male adapter (optional)
10. 3/8 female to 5/8 male adapter (optiona)
Steps:
1. Assemble the 3D printed clamp as described in Appendix B Assembly Instructions for 3D Printed Clamp.

2. Screw the 11" Inch Friction Articulating Magic Arm for Camera DSLR into the Mic Adapter in the 3D printed clamp.
3. Determine the length of the arrow shaft necessary by adjusting the articulating arm and approximating the length necessary to reach the mouth of the user. There will be two sections of arrow shafts in total.
4. Use the tube cutter to cut the arrow shaft to size. Make sure to file the ends of the arrow shaft to remove sharp edges.
Note: we found that increasing the length of the arrow shaft increases the vibration of the whole assembly, which makes it difficult to use the LipSync. The maximum suggested length arrow shaft to use is 9".
5. Glue the 3D printed 3/8-16 threaded holder on one end of an arrow shaft.
6. Screw in the 5/8 to 3/8 threaded adapter in the LipSync. Make sure to leave room for the LipSync spacer or to place the spacer in its position.
7. Screw the 3/8-16 threaded holder into LipSync to help with aligning the Disk Gear. Be careful not to over-tighten as to avoid breaking the threaded holder.
8. Place the Disk Gear at the other end of the arrow shaft. Make sure that the side of the disk is aligned with the LipSync as shown in the image below. Glue the arrow shaft in the Disk Gear.


Figure 15 - Disk Gear Aligned with the LipSync


Figure 16 - Misaligned Disk Gear
9. Grab the other arrow shaft and glue the 3D printed 1/4-20 threaded insert.
10. Place the Disk Gear at the other end of the arrow shaft and glue it in place.
11. Place the Articulating Magic Arm onto the arrow shaft with the 1/4-20 threaded insert by threading it into the arrow shaft. It is advisable to glue the 1/4-20 insert to the Articulating Magic Arm to provide stability to the assembly.
12. Glue the 5/16 in nut int the 3D printed hand knob.


Figure 17 - Glued Nut in 3D Printed Hand Knob
13. Attach the second arrow shaft to the first by meshing the Disk Gear together. Use the 5/16 in.-24 tpi x 1-1/2 in. Hex Cap Screw and the Hand Knob to tighten the disk. You can glue in the Hex Cap Screw to keep it in place.


Figure 18 - Disk Gear Used to Adjust the Angle of the Arrow Shafts
14. Use both the Disk Gear and the Articulating Arm to adjust the angle of the LipSync.

3D Printed Clamp; Articulating Arm; 1/4-20 Insert; Arrow Shafts; Disk Gear; 3/8-16 Insert

For the optional component:
15. Follow steps 1-4 outlined above.
16. Glue in the 3D printed 1/4-20 threaded insert on one end of an arrow shaft.
17. Glue in the bottom piece of the Disk Gear at the other end of the arrow shaft.
18. Grab the other arrow shaft and repeat step 2.
19. Glue the top piece of the Disk Gear at the other end of the arrow shaft.
20. Place the Mini Ball Head with Lock onto the other arrow shaft with the 1/4-20 threaded insert by threading it into the insert. It is advisable to glue the 1/4-20 insert to the Mini Ball Head with Lock to provide stability to the assembly.
21. Thread the 3/8 female to 5/8 male into the LipSync. Thread the 1/4 male to 3/8 male adapter into the adapter in the LipSync.
22. Thread the Mini Ball Head into the LipSync and adapter assembly.
23. Follow steps 12-13 outlined above.
24. Use the Disk Gear, Articulating Arm, and the Mini Ball Head to adjust the angle of the LipSync.

Mini Ball Head With Lock

Figure 19 - Complete Assembly of DIY Mount With Mini Ball Head


### Appendix D Field of Vision Claculations

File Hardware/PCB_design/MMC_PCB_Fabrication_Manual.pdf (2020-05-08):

# MMC PCB Fabrication Manual

Version 1.0
2020/05/05

Makers Making Change
PCB Fabrication Manual | PCB Fabrication Manual
Version 1.0 | Page 2 of 10

## Table of Contents

## 1. Introduction

## 1.1. What is PCB?

PCB (Printed circuit board) is a board that has lines and pads that connect various points together. The board includes traces that electrically connect the various connectors and components to each other. A PCB allows signals and power to be routed between physical devices. Solder is the metal that makes the electrical connections between the surface of the PCB and the electronic components. [1]

## 1.2. What is PCB Fabrication?

PCB fabrication is the assembly method for circuit boards used in electronic devices. The layers of the board are put together along with the specific surface pattern based on the design files that is used in electronics manufacturing.[2]

## 1.3. What is gerber file?

Users create their own files for manufacturing based on the design files and send them to the manufacturer. The design files for manufacturing PCB is converted to a standard format known as a Gerber file. This is an industry standard for recording the specification of a PCB.[2]

## 2. PCB design tools

There are many different tools for designing PCB’s and you can select any of the available tools based on your previous experience or the requirements of your design. The process of designing PCB is not in the scope of this document but you can find courses or books that can help you understand the process of designing electronics circuits and PCB’s.

Here are the most common PCB design tools:

- Altium Designer (https://www.altium.com/) : Paid with Free Trial and student license.
- Eagle (https://www.autodesk.ca/en/products/eagle/) : Free limited version includes 2 schematic sheets, 2 signal layers, and an 80cm2 (12.4in2) board area.
- Kicad (https://www.kicad-pcb.org/) : Opensource with GNU’s GPL copyright agreement.
- Fritzing (https://fritzing.org/) : Opensource version available on github and the paid application is available. Limited options suitable for basic designs.
- Upverter (https://upverter.com/) : Free cloud-based design tool. It requires sign up for usage.

There are other available tools that can be used to design PCBs.

## 3. How to generate PCB gerber files for fabrication?

Once the PCB board file is created using your favorite PCB design tool then you can generate gerber files which is used by PCB fabrication companies to fabricate your design. The CAM processing tool uses the gerber generator file to create gerber files. The gerber generator file is usually provided by PCB fabrication company of your choice or can be created based on gerber files format which can be found on the website of the PCB fabrication company.

Each PCB board file includes different top and bottom layers and gerber files provide specifications for each of these layers by combining layers together based on the format specified by gerber file generator.

Common layers:

- Top & Bottom Copper
- Top & Bottom Silkscreen
- Top & Bottom Soldermask
- Drill
- Drill Station Info
- Photoplotter Info
- Mill Layer
- Top Paste

There is no standard format for the gerber file generator and there are variations of formats used by PCB fabrication companies.

You can find the final generated gerber files of the projects involving PCB designs for common PCB fabrication companies on our website. You can use the generated gerber files available if you are using one of the fabrication companies listed below or you can create your own gerber files based on PCB design files.

- Seeed Fusion PCB (https://www.seeedstudio.com/fusion.html)
- PCBWay (https://www.pcbway.com/)
- OSH Park ~ (https://oshpark.com/)
- JLCPCB (https://jlcpcb.com/)

We now go over process of generating gerber files using three common PCB design tools.

## Eagle

1. Open the board file of your PCB design using Eagle
2. Select File > CAM Processor
3. Click on “Load job file” dropdown menu button and select “Open CAM file”
4. Download or create the gerber generator file (.cam) used by your PCB fabrication company of your choice
5. Navigate in your system and find the directory that includes the gerber file generator file with. cam extension
6. Select the gerber file generator file and click on “Open” button
7. Double check the Output file layers on left menu bar to make sure there are no layers are missing
8. Click on “Process Job” button
9. Select the output directory (Create a new directory called “gerbers” as an example)
10. The process of creating the gerber file will start and finish once you receive a popup message indicating that “Job Proceed Successfully!”
11. Click on “OK” button
12. Navigate to the directory that includes the generated gerber files (“gerbers” directory as an example)
13. Select all the gerber/drill files in the directory that saved them and generate a compressed file in Zip format.
14. You can now submit the compressed Zip file that includes the gerber files to the PCB fabrication company of your choice.

## Altium designer

1. Open the board file of your .PCB design file using Altium designer. [3]
2. Select File > Fabrication Outputs > Gerber Files
3. Select General setting in Gerber Setup window
4. Set the units in “inches” precision to “2:5” in General setting
5. Select Layers setting in Gerber Setup window
6. Next, make sure you have the clear outline in mechanical layer.

7. Check the layers in “Plot” column under “Layers To Plot” section for creating gerber files according to fabrication company instructions.
- Check following layers: GTO, GTP, GTS, GTL, GBL , GBS , GBP , GBO , GKO ,GPT , GPB , GM(Number)
- There will be no middle layer if you PCB board includes only 2-layers. All our design files include 2 layers which means you need to uncheck all middle layers (G1,G2,G3....)
- You can use the “Plot Layer” option and select the “Used On” to automatically check the used layers in your design.
8. Select “All Off” in “Mirror Layers” or uncheck every layer in “Mirror Layers” column
9. Uncheck all the layers in the plot column of “Mechanical Layers to Add to All Gerber Plots”
10. Check “Embedded apertures (RS274X)” under “Aperture” setting
11. Click on the “OK” button to generate gerber files.
12. Gerber files are automatically loaded in the Altium cam viewer. You can use “CAMtastic” view to verify that all layers have been generated correctly.
13. The gerber files should now be generated and saved in directory of your project.
14. You can also export gerber files to a new directory using following steps:
- Select File > Export > Gerber…
- Click on “OK”
- Select the path to the directory that you would like to save all the gerber files. (“gerbers” directory as example)
- Click on “OK” to export all the gerber files
15. Next, Generate the Drilling layer in Excellon format
16. Select File > Fabrication Outputs > NC Drill Files
17. Set the units in “inches” precision to “2:5” in NC Drill Setup window
18. Click on the “OK” button to generate drill files
19. The drill file should now be generated and saved as .TXT file in directory of your project.
20. You can also export file to a new directory using following steps:
- Select File > Export > Save Drill…
- Click on “OK”
- Select the path to the directory that you would like to save the drill file. (“gerbers” directory as example)
- Click on “OK” to export the drill file
21. Select the “Projects” view and highlight the “CAMtastic” cam file
22. Click on “Save As” under “File” and save the “CAMtastic” cam file.
23. Click on “Save”.
24. Select all the gerber/drill files in the directory that saved them and generate a compressed file in Zip format.

25. You can now submit the compressed Zip file that includes the gerber files to the PCB fabrication company of your choice.

## Kicad

1. Open the board file of your design file using Kicad. [4]
2. Select File > Plot
3. Check the layers in “Plot” window for creating gerber files according to fabrication company instructions.
- Check following layers: Top Copper (F.Cu), Soldermask (F.Mask), Silkscreen (F.SilkS), Bottom Copper (B.Cu), Soldermask (B.Mask), Silkscreen (B.SilkS), Board outline (Edge.Cuts)
4. Set the “Output directory” to save the generated gerber files. You can also use “Browse…” button to set the path to the directory.
5. Uncheck “Plot sheet reference on all layers” option.
6. Uncheck “Plot footprint values” option.
7. Check “Exclude PCB edge layer from other layers” option.
8. Check “Use Protel filename extensions” option.
9. Click on “Plot” button to generate and save gerber files in the specified output directory to save gerber files.
10. Next, configure the settings to generate drill file
11. Click on “Generate Drill File” button.
12. Set the “Output directory” to save the generated drill file. You can also use “Browse…” button to set the path to the directory. Use the same output directory as you selected to save the gerber files.
13. Check “Inches” as drill units.
14. Check “Decimal Format” as zeros format.
15. Check “PostScript” as drill map file format.
16. Check the “Merge PTH and NPTH holes into one file” option
17. Click on “Drill File” or press “Enter” to generate the drill file.
18. Click on “Close” to close “Drill Files Generation” Window.
19. Click on “Close” again to close “Plot” Window.
20. Verify the generated gerber files using a gerber viewer tool to make sure that all layers have been generated correctly.
21. Select all the gerber/drill files in the directory that saved them and generate a compressed file in Zip format.
22. You can now submit the compressed Zip file that includes the gerber files to the PCB fabrication company of your choice.

## 4. How to check and confirm PCB gerber files?

It is recommended to double check or triple check the final generated gerber files of your design to make sure there are no issues with process of gerber files generation. The PCB fabrication companies mostly provide online gerber file viewer tools that you can use to confirm your design once you upload your gerber files compressed as a Zip file. However, you can use other gerber file viewer to check your design files before submitting the gerber files.

The following gerber viewer tools are recommended:

- Online Gerber Viewer (https://www.gerber-viewer.com/)
- gerbv (https://sourceforge.net/projects/gerbv/)

Select all the generated gerber file layers in the “gerbers” directory and view them to make sure all the layers are aligned.

## 5. Where to send PCB gerber files for fabrication?

The process to send the gerber files for fabrication may differ from company to company but there are general steps you can follow to send your gerber files for fabrication.

1. Select the fabrication company (Here are our recommended fabrication companies)
- Seeed Fusion PCB
- PCBWay
- OSH Park ~
- JLCPCB
2. Create an account on PCB fabrication website or use temporary login if it is available
3. Select the fabrication service
4. Upload the compressed Zip file that includes your gerber files
5. Select the available options based on your design requirements. The standard options for most of our projects:
- PCB Layers: 2 Layers
- PCB dimensions should update based on your uploaded gerber files, but you can manually entry the dimensions as well
- PCB quantity can vary based on your requirements (Minimum 5)
- PCB Color can be changed if the fabrication company offers the option. The defualt option has the fastest turnaround time.
- Surface Finish: HASL
- Copper Weight, Minimum Drill Hole Size, Trace Width , Minimum Solder Mask Dam doesn’t require to be changed and the default value works
6. Check the uploaded gerber files using online gerber viewer tool if it is offered by the fabrication company and make sure there are no issues.

7. Add the uploaded design to the order
8. Add another design if you are doing multiple orders
9. Proceed to the checkout and enter your billing and shipment information
10. Select the shipping method
11. Submit your order for production
12. The technician will contact you for additional information or corrected files if there are issues with your design files.
13. You will receive an email when your design goes to production
14. You will receive another email once your PCBs are produced and shipped

This includes the instructions for fabrication of PCB designs based on generated gerber files.

## Reference

1. https://learn.sparkfun.com/tutorials/pcb-basics/all
2. https://www.hi5electronics.co.uk/what-is-pcb-fabrication/
3. https://support.jlcpcb.com/article/42-how-to-export-altium-pcb-to-gerber-files
4. https://support.jlcpcb.com/article/44-how-to-export-kicad-pcb-to-gerber-files

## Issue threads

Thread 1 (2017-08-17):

### ISSUE TITLE
LED 4 and 5 are not assigned to the correct constant

### ISSUE THREAD

**Issue by markingle** [makersmakingchange/LipSync-Classic#1]
#define LED_1 **4**                                   // LipSync LED Color1 : GREEN - digital output pin 5
#define LED_2 **5**                                   // LipSync LED Color2 : RED - digital outputpin 4

Should be .....

#define LED_1 **5**                                   // LipSync LED Color1 : GREEN - digital output pin 5
#define LED_2 **4**                                  // LipSync LED Color2 : RED - digital outputpin 4

**Comment by makersmakingchange** [comment]
Hi Mark,
I am going to close this issue as the variables are assigned correctly.

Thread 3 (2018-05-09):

### ISSUE TITLE
Part 26 has a 404 link

### ISSUE THREAD

**Issue by ctag** [makersmakingchange/LipSync-Classic#3]
Hi,

In the manual, the [Mouthpiece part](http://www.qosina.com/male-luer-lock-stepped-connector-11648) takes me to a "product not found" page on Qosina's website.

Would [this part](https://www.qosina.com/stepped-male-luer-lock-connector-80102) be a suitable replacement?

Thanks,
Chris

**Comment by makersmakingchange** [comment]
Hi Chris,

Thanks for catching this. You are correct about the mouthpiece. We contacted Qosina, the link you found (SKU: 80102) is the replacement for the previous one. The link is updated in Manual v.1.4.6

Thanks!

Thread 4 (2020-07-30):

### ISSUE TITLE
Headers not reaching in step 46 of assembly

### ISSUE THREAD

**Issue by ctag** [makersmakingchange/LipSync-Classic#4]
Hi,

I'm at the tail end of assembling a lipsync, and have hit a small roadblock. Step 46 in the manual shows joining the joystick input onto the main PCB. When I try to do this, the headers just *[barely](https://lh3.googleusercontent.com/-HzDvTFKiTPs4Q3U8kpLXTWcPFMRZtS6OtpZfv3VrYSGvlZRsmPxdE6zdAhsjINIq8nM0WegqKW7vgM3H8OEQwK9bu-DROiDsiqMQHMnjDnIxqmINXWQZl38aM0Gi0g8xnji6cWNvCtDMhDniQn_GvPznPVhrXtDz6Lk0yiw5tF2zVp4Xqr8-Ndb2lhKOlgLu283Etzqd2gsMgY9rRNgOvsjvHW8KYzZf_m3EBcSYTXbwPBonm5OGFSADbklnt6JssEMPtlCppNgmtlF1SCmGRc3a79JIT2K9ro4Ktno046k104-RLC7nrI0yqNmCLkPhakF1mqQCSRqFbXuISUqnmZ-qAARwxpwyUrDOy8qILJqgdyt1xg64l7FCB7AegzQ-UdPYlkpJ51PcGy9UY0Od8dYBS05BZNpyt0ALCffYN-3-FkpJWQePbKxkZeqrGjp3NsC86aRNtH3U7XGeZQ6GRtzNLt-WrFsuX61oYIV6rgaKQyuOEwF5rj4aCnPcuy_crPsSqgiXqwjjBdL-_Z0DPpU464crkgGK9ZTdSAfJGMwY9TNBFeKbMZm-w07cDzgIPg_hLTLVkgbFrQhIPji7mB7zcZy9ECg0ERDlsRe26Q1Vu7eGPZqD0Zlpx-I7A0ok3Ibmz9gXKxL43OZXadcXSOUUC3xIztQ=w3201-h1602-no)* reach, and I doubt they will stay joined through prolonged use. Not unexpected, since the right angle headers are just from a drawer in my office. 

My first guess to address this is to just solder the headers together, if the system needs to be serviced later they'll have to be removed and possibly replaced. **But** in Step 47 there's.. something else there. I can't tell from the picture, but it looks like the headers have been boosted another mm by something. Is there any documentation you can give me about that, or am I looking at the image wrong?

Thanks!

**Comment by hpigot** [comment]
Hey ctag, I noticed the same issue and had the same thoughts (using parts directly from MakersMakingChange/NSS). It seems like the part (female headers) changed, but the assembly manual images weren't brought up to date. They do make a special comment about ONLY using those female headers from DigiKey, but I'm not sure what motivated the change.
![image](https://user-images.githubusercontent.com/22122190/43164889-b417e34e-8f92-11e8-9502-08843ce0328e.png)

The device did work as-is, but I cannot comment on the long-term functionality. Perhaps @igourlay can comment on this?

**Comment by milador** [comment]
Hi ctag and hpigot, I am one of the engineers from MakersMakingChange/NSS.

Thank you for bringing up the issue. The images in step 47 are from older version of LipSync PCBs (Version 2.5). We used right-angle female headers and straight male headers to connect main board to joystick board in version 2.5.

We switched to right-angle male headers and straight female headers instead in version 2.6.
You would need to use the headers specified in the list of components as not all the common headers would work due to their height difference.

I hope it helps and we will update the pictures in step 47 in the next update.

**Comment by hpigot** [comment]
Thanks for the input milador. Perhaps in 2.7 the connection between the headers could be made more deeply; at the moment the male headers barely touch the female headers and it does seem out of place during construction.

**Comment by milador** [comment]
@hpigot Thank you for your feedback.We will look into it and update you.

**Comment by ctag** [comment]
Thank you for the responses. I'm glad I wasn't going crazy looking at those pictures.

As hpigot wrote, the headers just barely reach. I did use the vertical female headers linked to in the manual (part #12) but used generic right angle male headers (part #11).

Since I plan to hold on to this lipsync as a reference when making future ones, I went ahead and [soldered the joint for now](https://lh3.googleusercontent.com/3P8OnEv3PJSzcNVY25qphE0EQzSgjAcXkquns4NXm3_3wWt2QPPuaNxUH0YX04YDXlKZLpmQgE_wDAF9Sjag_rvHZCmwtjYCX4f0OsWeobROQn48OZpCxLdjUqaUag6aRAb_4zmW99Zk18i-UkyIsl5VShYhL0fnRuKXyPJ2_XSTfJ2oFSnYa7tQRNrydXnjw_Fp3ncasW3TB6PBrvYEsl7zXH8CiDXzQDYd5fiwYldPvZdjcg4HfzEg2e11ZxucvWHDAEl4qyvBjkN3MmXI0PNDnV_1K-VKnZd3IfAn5oGOfpLH5O_XDUVMm3ElKziQg6LD5Fbk7ZSAAGR5zSdem2m_XFYFWFmfDH9rgjotMkvNW8DHSgaBxJUNGfKsr5V2g8ZZAr6kpix1XydUTWe8Fz-iyN3nAU9irgP2V568oFqn5oLjWRulvTfwdFRy7LgTGdPwM13OswgsWuKKSlSaqBsl4ixSr7p-tXpL3IHLGdhn7tlKWUeu5_DeB8wUY290ElJE5iK8mDNNHA4nmg15M8D_qWj3O19b-Iez7H1wdck-4YYTHaUdhZFcPce84eJ12CRHo46zAHiEyp8Am7tKdqBWHzJxv6zYIUlQNy4=w3201-h1602-no), which seems to work nicely.

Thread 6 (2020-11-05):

### ISSUE TITLE
Sources for PDFs are not available in this repo?

### ISSUE THREAD

**Issue by d3r3kk** [makersmakingchange/LipSync-Classic#6]
There are a few places where I could help out in the documentation of the LipSync device. However, the LipSync repo only contains PDFs and not any editable sources (I don't own a license for any Adobe products, perhaps that is the prerequisite to updating the docs).

It would be great to have easily editable documentation in a format such as Markdown or similar, and then a process by which that input format can be transformed into other formats such as PDF.

Proposal for this might look like:

- Create a `/doc/` folder in the repo.
- Re-create the PDF content in a Markdown file each and save them in the `/doc/` folder.
- Add a script that allows people to use tools such as [Pandoc](https://pandoc.org/) to convert them to PDF.
- Consider a 'release' process that would create a zip file containing the PDF documentation.

**Comment by milador** [comment]
Excellent idea Derek @d3r3kk . @MMC-km is in charge of documentation and visual aspect so I let her perform the changes.
I started the [md files](https://github.com/makersmakingchange/LipSync/tree/develop/Documentation) in develop branch which could be a good start.

**Comment by MMC-km** [comment]
Hi @d3r3kk . I uploaded the original .docx files to the folder @milador created. The assembly manual was created with InDesign but if you want to share a list of feedback for that, I can incorporate it in our next round of manual changes. Hope that helps!

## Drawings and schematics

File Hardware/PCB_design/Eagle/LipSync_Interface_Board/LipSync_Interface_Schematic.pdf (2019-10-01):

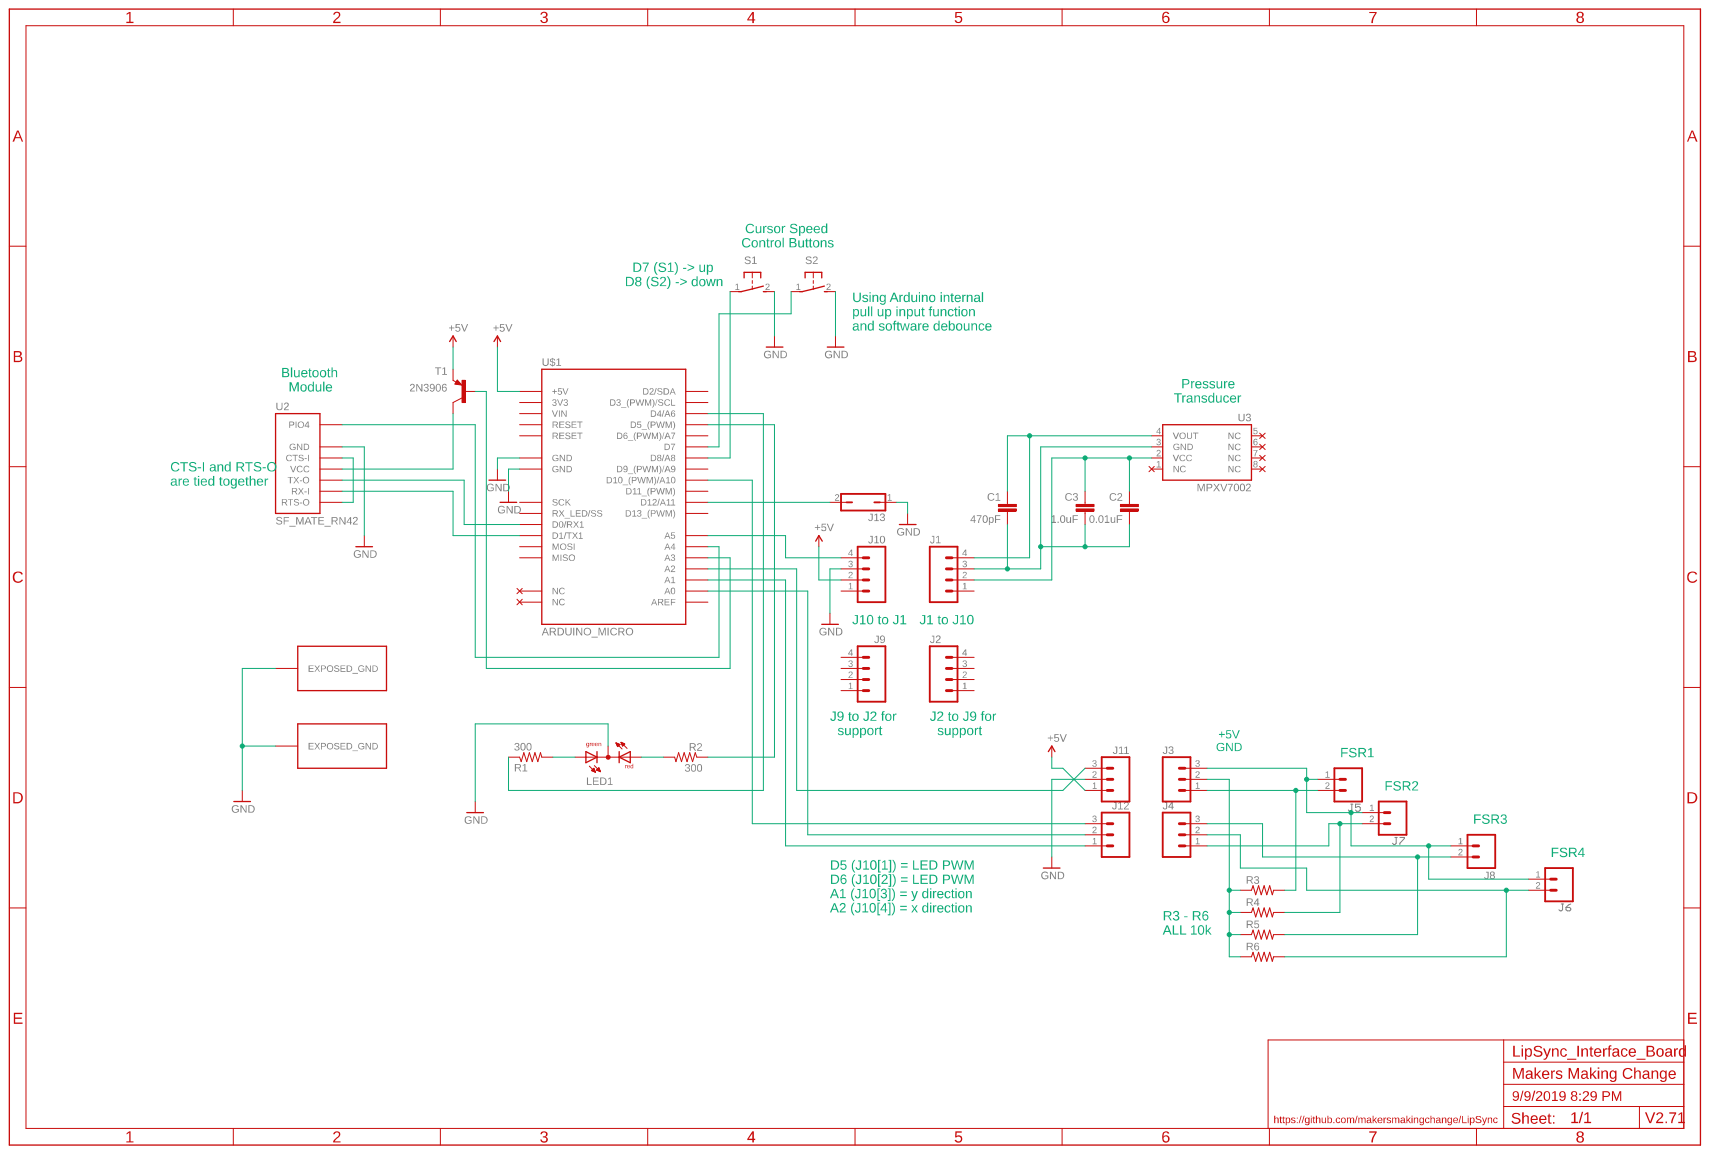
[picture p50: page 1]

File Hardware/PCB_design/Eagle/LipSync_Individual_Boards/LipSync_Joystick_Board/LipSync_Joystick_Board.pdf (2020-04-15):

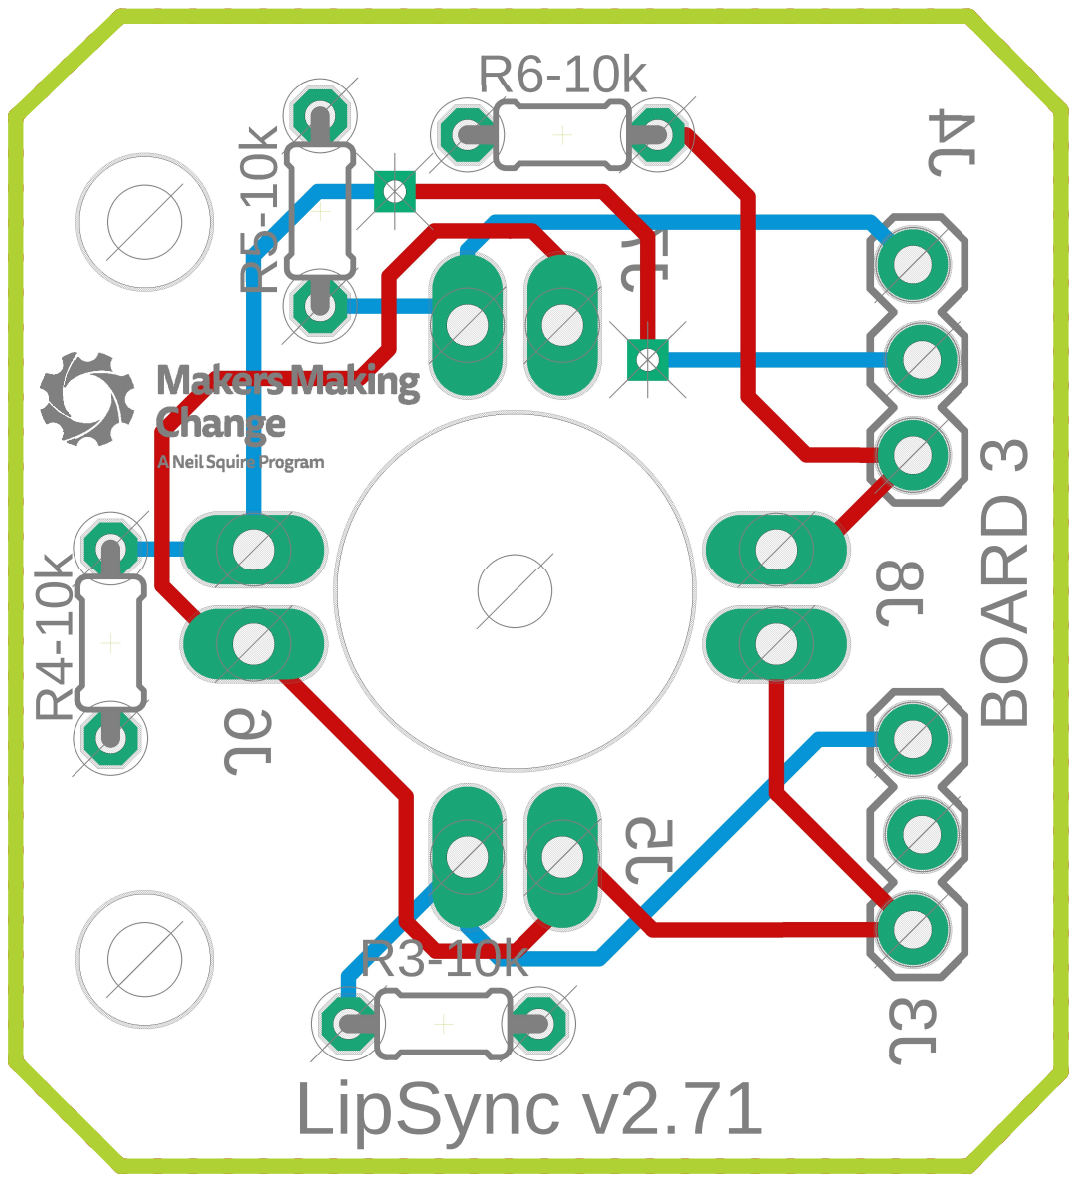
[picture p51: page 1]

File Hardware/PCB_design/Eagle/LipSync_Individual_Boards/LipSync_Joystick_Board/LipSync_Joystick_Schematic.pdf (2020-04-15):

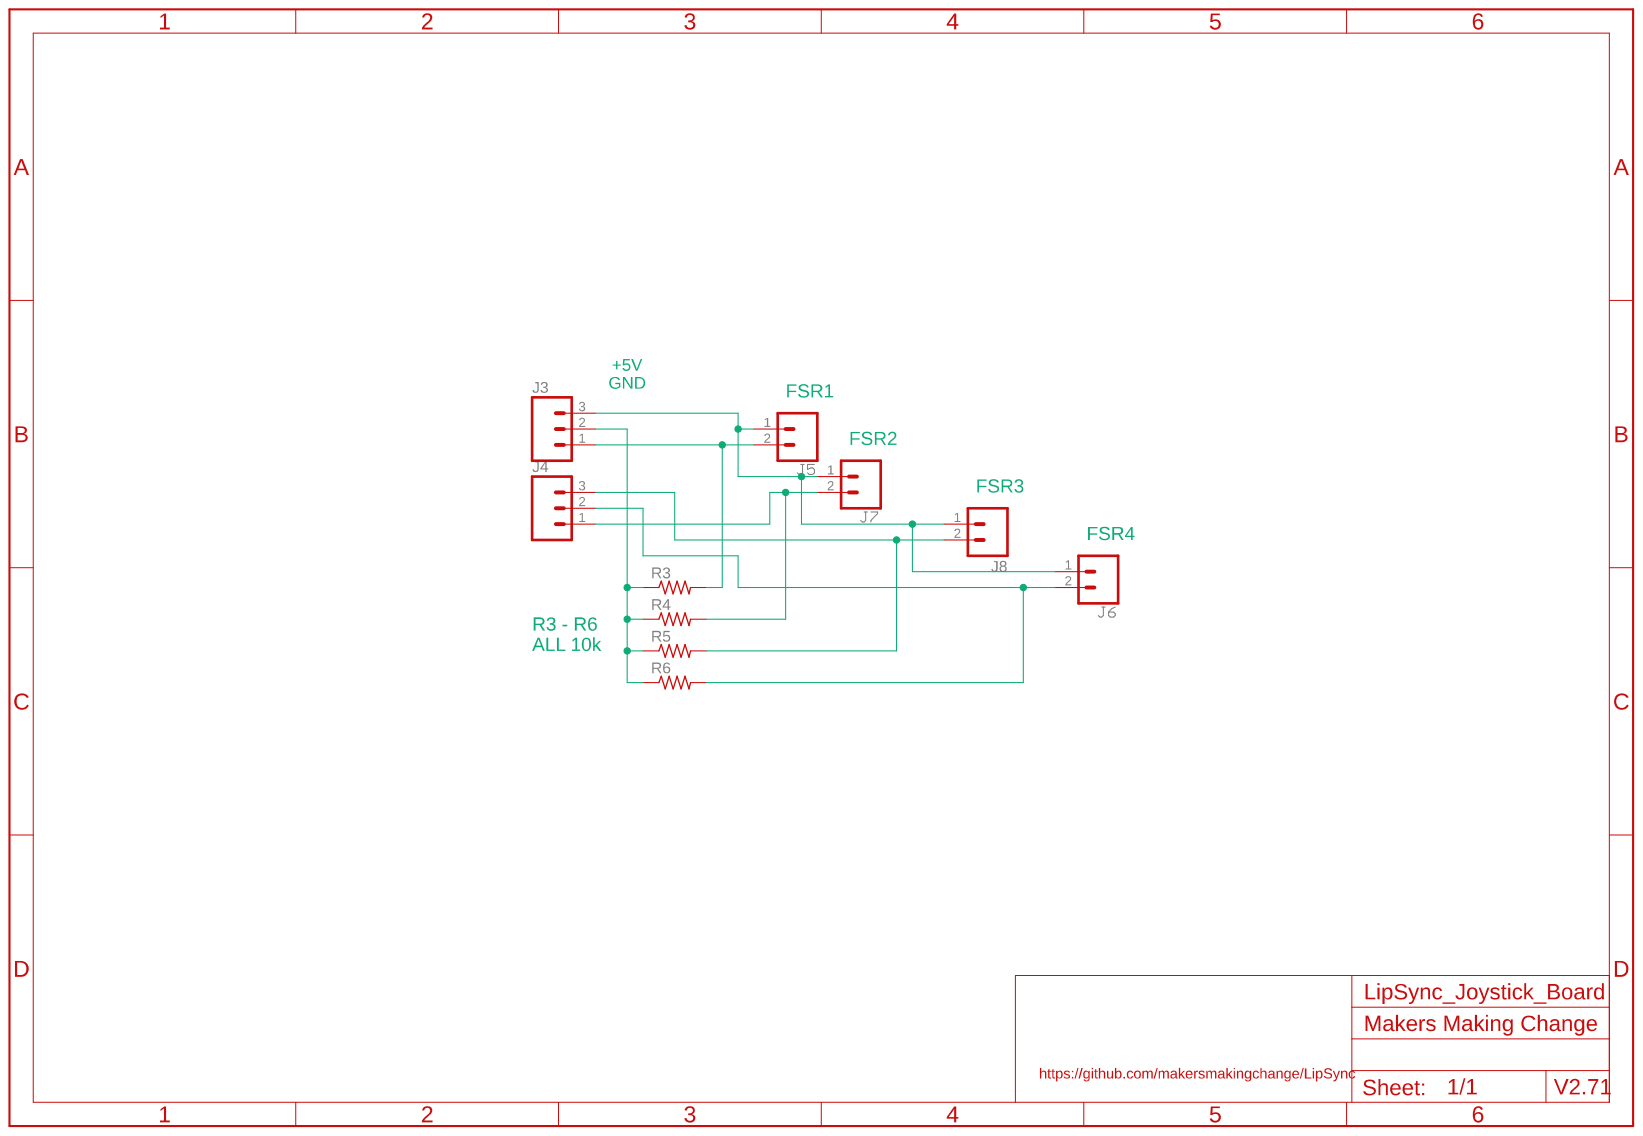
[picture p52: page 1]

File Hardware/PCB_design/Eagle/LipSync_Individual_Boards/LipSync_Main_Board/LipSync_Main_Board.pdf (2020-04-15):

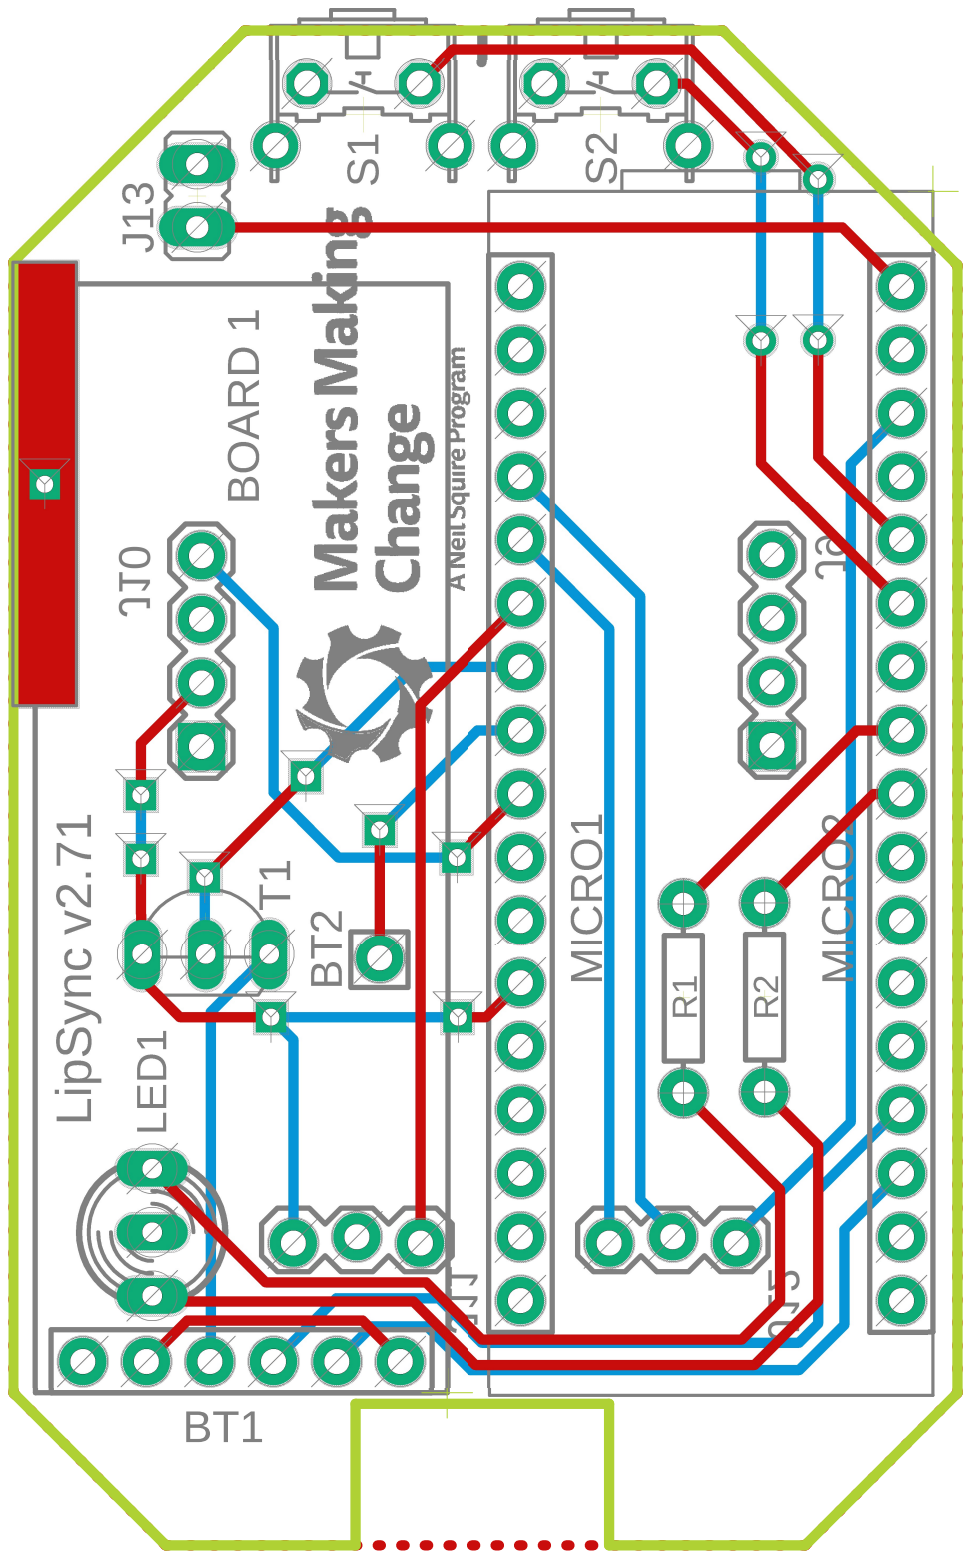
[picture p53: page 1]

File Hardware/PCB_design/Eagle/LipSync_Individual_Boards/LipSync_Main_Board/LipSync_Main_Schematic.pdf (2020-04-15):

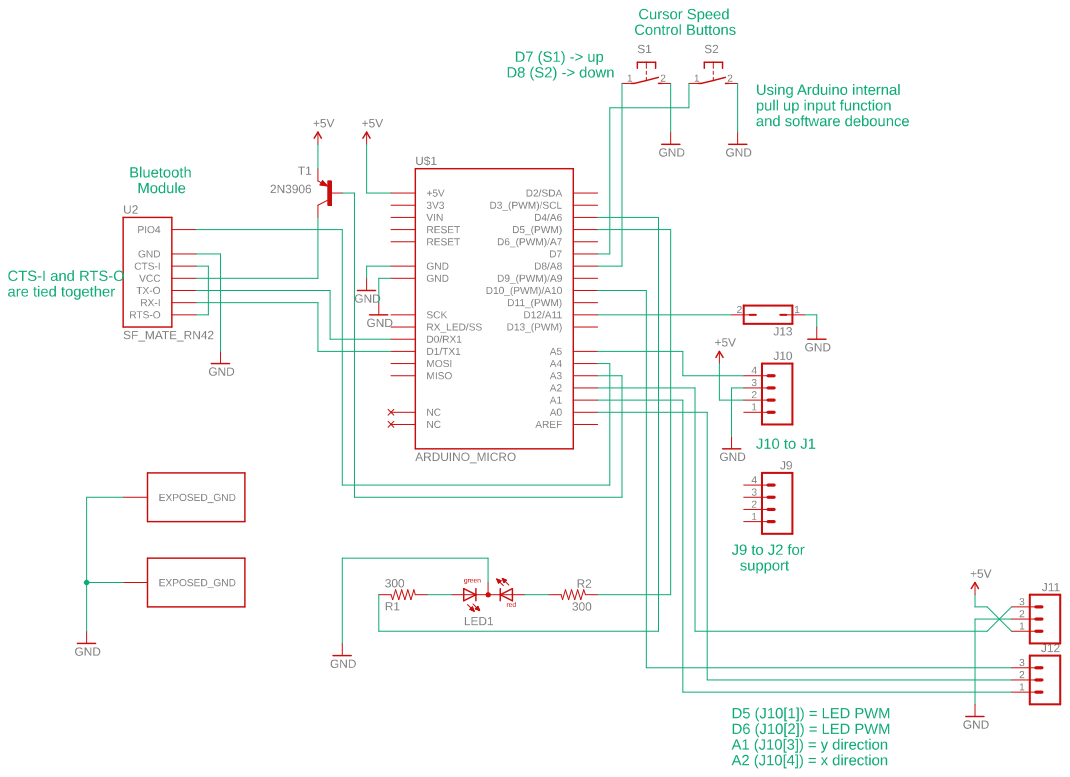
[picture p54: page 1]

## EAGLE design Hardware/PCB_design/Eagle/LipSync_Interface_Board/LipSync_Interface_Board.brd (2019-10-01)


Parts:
C1: 470pF; CAP-PTH-SMALLEZ
C2: 0.01uF; CAP-PTH-SMALLEZ
C3: 1.0uF; CAP-PTH-SMALLEZ
J1, J2, J9, J10: M04PTH; 1X04
J3, J4, J11, J12: M03LOCK; 1X03_LOCK
J5, J6, J7: CONN_02PTH3; 1X02_LONGPADS
J8: M02PTH3; 1X02_LONGPADS@1
J13: JP1Q; JP1
LED1: DUOLED-RG-C; DUOLED-C-5MM
R1, R2: 300; AXIAL-0.3
R3, R4, R5, R6: R-US_0204/5; 0204/5
S1, S2: 31-XXB3F-31XX-CUSTOM; B3F-31XX-CUSTOM
T1: 2N3906; TO92-EBC
U2: SF_MATE_RN42; BLUE_MATE_RN42_HEADER_FOOTPRINT
U3: MPXV7002; SOP8
U$1: ARDUINO_MICRO; ARDUINO_MICRO_HEADER_FOOTPRINT
U$2, U$3: EXPOSED_GND

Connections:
3V3: U$1.3V3
GND: J10.3, J11.2, J13.1, LED1.C, S1.2 (S), S2.2 (S), U2.GND, U$1.GND, U$1.GND@1 (GND), U$2.GND1, U$3.GND1
GND2: C1.2, C2.2, C3.2, J1.3, U3.3 (GND)
GND3: J3.2, R3.1, R4.1, R5.1, R6.1
unnamed: U2.PIO4, U$1.A4
unnamed: T1.C, U2.VCC
unnamed: U2.TX-O, U$1.RX1 (D0/RX1)
unnamed: U2.RX-I, U$1.TX1 (D1/TX1)
unnamed: J12.2, U$1.A0
unnamed: J12.1, U$1.A1
unnamed: C1.1, J1.4, U3.4 (VOUT)
unnamed: C2.1, C3.1, J1.2, U3.2 (VCC)
unnamed: U2.CTS-I, U2.RTS-O
unnamed: J12.3, U$1.D10 (D10_(PWM)/A10)
unnamed: J10.4, U$1.A5
unnamed: LED1.AX (AG), R1.P$2 (2)
unnamed: LED1.AR, R2.P$2 (2)
unnamed: S1.1, U$1.D8 (D8/A8)
unnamed: S2.1, U$1.D7
unnamed: J3.3, J5.1, J6.1, J7.1, J8.1
unnamed: R1.P$1 (1), U$1.D4 (D4/A6)
unnamed: R2.P$1 (1), U$1.D5 (D5_(PWM))
unnamed: T1.B, U$1.A3
unnamed: J11.3, U$1.A2
unnamed: J3.1, J5.2, R3.2
unnamed: J13.2, U$1.D12 (D12/A11)
unnamed: J4.1, J7.2, R4.2
unnamed: J4.3, J8.2, R5.2
unnamed: J4.2, J6.2, R6.2
VCC: J10.2, J11.1, T1.E, U$1.5V (+5V)

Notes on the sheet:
J9 to J2 for support
J2 to J9 for support
D5 (J10[1]) = LED PWM D6 (J10[2]) = LED PWM A1 (J10[3]) = y direction A2 (J10[4]) = x direction
CTS-I and RTS-O are tied together
J1 to J10
J10 to J1
Cursor Speed Control Buttons
D7 (S1) -> up D8 (S2) -> down
+5V GND
Bluetooth Module
Pressure Transducer
Using Arduino internal pull up input function and software debounce
R3 - R6 ALL 10k
FSR1
FSR2
FSR3
FSR4
Makers Making Change
V2.71
https://github.com/makersmakingchange/LipSync



Board: 2 copper layers, 69.1 x 60.7 mm, 31 parts (11 on the bottom side), 29 nets.

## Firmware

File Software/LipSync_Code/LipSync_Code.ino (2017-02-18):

/*
  ----------------------------------------------------------
  =    //        //            ///               ///       =
  =    ////      //         ///  ///         ///    ///    =
  =    // //     //         ///              ///           =
  =    //  //    //          ///              ///          =
  =    //   //   //            ///              ///        =
  =    //    //  //              ///              ///      =
  =    //     // //               ///              ///     =
  =    //      ////        ///   ///         ///   ///     =
  =    //       ///           ///               ///        =
  ----------------------------------------------------------
*/

//AUTHOR: Ivan Gourlay 22 June 2016

/*
   REVISION HISTORY:
   27 Jun 2016
   08 Jul 2016
   11 Jul 2016
   15 Jul 2016
   18 Jul 2016
   29 Jul 2016
   02 Aug 2016
   03 Aug 2016
   16 Aug 2016
   18 Aug 2016
   25 Aug 2016
   26 Aug 2016
   27 Aug 2016
   29 Aug 2016
   30 Aug 2016
   04 Sept 2016
   13 Sept 2016
   14 Sept 2016
   19 Sept 2016
   26 Sept 2016
   27 Sept 2016
   29 Sept 2016
   06 Oct 2016
   12 Oct 2016
   17 Oct 2016
   25 Oct 2016
   04 Nov 2016
   07 Nov 2016
   ---
   30 Nov 2016
   02 Dec 2016
   12 Dec 2016
   13 Dec 2016
   14 Dec 2016
   15 Dec 2016
   20 Dec 2016
   23 Dec 2016
   24 Dec 2016
   30 Dec 2016
   03 Jan 2017
   10 Jan 2017
   19 Jan 2017
   22 Jan 2017
   26 Jan 2017
*/

#include <EEPROM.h>
#include <Mouse.h>
#include <math.h>

//***PIN ASSIGNMENTS***//

#define MODE_SELECT 12                            // LipSync Mode Select - USB mode (comm_mode = 0; jumper on) or Bluetooth mode (comm_mode = 1; jumper off) - digital input pin 12 (internally pulled-up)
#define PUSH_BUTTON_UP 8                          // Cursor Control Button 1: UP - digital input pin 8 (internally pulled-up)
#define PUSH_BUTTON_DOWN 7                        // Cursor Control Button 2: DOWN - digital input pin 7 (internally pulled-up)
#define LED_1 5                                   // LipSync LED Color1 - digital output pin 5
#define LED_2 4                                   // LipSync LED Color2 - digital outputpin 4

#define TRANS_CONTROL A3                          // Bluetooth Transistor Control Pin - digital output pin A3
#define PIO4 A4                                   // Bluetooth PIO4 Command Pin - digital output pin A4

#define PRESSURE_CURSOR A5                        // Sip & Puff Pressure Transducer Pin - analog input pin A5
#define X_DIR_HIGH A0                             // X Direction High (Cartesian positive x : right) - analog input pin A0
#define X_DIR_LOW A1                              // X Direction Low (Cartesian negative x : left) - digital output pin A1
#define Y_DIR_HIGH A2                             // Y Direction High (Cartesian positive y : up) - analog input pin A2
#define Y_DIR_LOW A10                             // Y Direction Low (Cartesian negative y : down) - analog input pin A10

//***VARIABLE DECLARATION***//

int xh, yh, xl, yl;                               // xh: x-high, yh: y-high, xl: x-low, yl: y-low
int x_center, y_center;                           // the relative x,y resting center of the joystick
int x_box_right, x_box_left, y_box_up, y_box_down;// boundaries for which x,y values must exceed to produce cursor movement
int box_delta;                                    // the delta value for the boundary range in all 4 directions about the x,y center
int cursor_delta;                                 // amount cursor moves in some single or combined direction
int speed_counter = 4;                            // cursor speed counter
int cursor_click_status = 0;                      // value indicator for click status, ie. tap, back and drag
int comm_mode = 0;                                // 0 == USB Communications or 1 == Bluetooth Communications
int config_done;                                  // Binary check of completed Bluetooth configuration
unsigned long puff_count, sip_count;              // long puff and long sip incremental counter

int poll_counter = 0;                             // cursor poll counter
int init_counter = 0;                             // serial port initialization counter
int calibration_counter = 0;                      // automatic calibration counter [self-correcting]

int default_cursor_speed = 100;
int delta_cursor_speed = 15;

int cursor_delay;
float cursor_factor;
int cursor_max_speed;

float yh_comp = 1.0;
float yl_comp = 1.0;
float xh_comp = 1.0;
float xl_comp = 1.0;

float yh_check, yl_check, xh_check, xl_check;

float sip_threshold, puff_threshold, cursor_click, cursor_back;

typedef struct {
  int _delay;
  float _factor;
  int _max_speed;
} _cursor;

_cursor setting1 = {5, -1.4, default_cursor_speed - (4 * delta_cursor_speed)}; // 5,-1.0,10
_cursor setting2 = {5, -1.4, default_cursor_speed - (3 * delta_cursor_speed)}; // 5,-1.2,10
_cursor setting3 = {5, -1.4, default_cursor_speed - (2 * delta_cursor_speed)};
_cursor setting4 = {5, -1.4, default_cursor_speed - (delta_cursor_speed)};
_cursor setting5 = {5, -1.4, default_cursor_speed};
_cursor setting6 = {5, -1.4, default_cursor_speed + (delta_cursor_speed)};
_cursor setting7 = {5, -1.4, default_cursor_speed + (2 * delta_cursor_speed)};
_cursor setting8 = {5, -1.4, default_cursor_speed + (3 * delta_cursor_speed)};
_cursor setting9 = {5, -1.4, default_cursor_speed + (4 * delta_cursor_speed)};

_cursor cursor_params[9] = {setting1, setting2, setting3, setting4, setting5, setting6, setting7, setting8, setting9};

//float cursor_factor = {-1.0, -1.2, -1.4, -1.6, -1.8, -2.0};

int single = 0;
int puff1, puff2;

//-----------------------------------------------------------------------------------------------------------------------------------

//***MICROCONTROLLER AND PERIPHERAL MODULES CONFIGURATION***//

void setup() {

  Serial.begin(115200);                           // setting baud rate for serial coms for diagnostic data return from Bluetooth and microcontroller ***MAY REMOVE LATER***
  Serial1.begin(115200);                          // setting baud rate for Bluetooth module

  pinMode(LED_1, OUTPUT);                         // visual feedback #1
  pinMode(LED_2, OUTPUT);                         // visual feedback #2
  pinMode(TRANS_CONTROL, OUTPUT);                 // transistor pin output
  pinMode(PIO4, OUTPUT);                          // command mode pin output

  pinMode(PRESSURE_CURSOR, INPUT);                // pressure sensor pin input
  pinMode(X_DIR_HIGH, INPUT);                     // redefine the pins when all has been finalized
  pinMode(X_DIR_LOW, INPUT);                      // ditto above
  pinMode(Y_DIR_HIGH, INPUT);                     // ditto above
  pinMode(Y_DIR_LOW, INPUT);                      // ditto above

  pinMode(MODE_SELECT, INPUT_PULLUP);             // LOW: USB (default with jumper in) HIGH: Bluetooth (jumper removed)
  pinMode(PUSH_BUTTON_UP, INPUT_PULLUP);          // increase cursor speed button
  pinMode(PUSH_BUTTON_DOWN, INPUT_PULLUP);        // decrease cursor speed button

  pinMode(2, INPUT_PULLUP);
  pinMode(3, INPUT_PULLUP);
  pinMode(9, INPUT_PULLUP);
  pinMode(11, INPUT_PULLUP);
  pinMode(13, INPUT_PULLUP);

  Serial_Initialization();
  delay(10);
  Set_Default();                                  // should only occur once per initialization of a new microcontroller
  delay(10);
  Pressure_Sensor_Initialization();               // register nominal air pressure and generate activation threshold boundaries
  delay(10);
  Joystick_Initialization();                      // home joystick and generate movement threshold boundaries
  delay(10);
  Communication_Mode_Status();                    // identify the selected communication mode
  delay(10);
  Mouse_Configure();                              // conditionally activate the HID mouse functions
  delay(10);
  BT_Configure();                                 // conditionally configure the Bluetooth module [WHAT IF A NEW BT MODULE IS INSTALLED?]
  delay(10);
  cursor_speed_value();                           // reads saved cursor speed parameter from EEPROM
  delay(10);

  int exec_time = millis();
  Serial.print("Configuration time: ");
  Serial.println(exec_time);

  blink(4, 100, 3);                               // end initialization visual feedback

  cursor_delay = cursor_params[speed_counter]._delay;
  cursor_factor = cursor_params[speed_counter]._factor;
  cursor_max_speed = cursor_params[speed_counter]._max_speed;

  // functions below are for diagnostic feedback only

  Serial.print("config_done: ");
  Serial.println(EEPROM.get(0, puff1));
  delay(5);
  Serial.print("speed_counter: ");
  Serial.println(EEPROM.get(2, puff2));
  delay(5);
  Serial.print("cursor_delay: ");
  Serial.println(cursor_params[puff2]._delay);
  delay(5);
  Serial.print("cursor_factor: ");
  Serial.println(cursor_params[puff2]._factor);
  delay(5);
  Serial.print("cursor_max_speed: ");
  Serial.println(cursor_params[puff2]._max_speed);
  delay(5);
  Serial.print("yh_comp factor: ");
  Serial.println(EEPROM.get(6, yh_check));
  delay(5);
  Serial.print("yl_comp factor: ");
  Serial.println(EEPROM.get(10, yl_check));
  delay(5);
  Serial.print("xh_comp factor: ");
  Serial.println(EEPROM.get(14, xh_check));
  delay(5);
  Serial.print("xl_comp factor: ");
  Serial.println(EEPROM.get(18, xl_check));
  delay(5);

}

//-----------------------------------------------------------------------------------------------------------------------------------

//***START OF INFINITE LOOP***//
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

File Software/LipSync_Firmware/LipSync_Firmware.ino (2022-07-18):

/*
  *                 `.:/++`             ....``
  *              `/ossss: `.`         `--------.`
  *               /ssso. .----..```..-----------                                                                                                                                  ``
  *               -ss+``-----------------------.                  ssss       -/++/`              /ss-                                     ./++/-      //+//             oss       `oss-
  *              `os+ `----------------.......--`                 sssss:    `s400s.              +sH-                                     -sBsss`    :ssBCs             sVs        /++`
  *    ``      .:ss+ `-------..```````````````````                sso+ss`   +so/ss.   -:::::.    +se-  `---  `-::::.  `-:`.::. .::::-     -su/ss+   `ss:sss  `-::::-`   s5s   .--. ---  .-- -:::-    .::::---.
  *   .oso+++oossso``---..``          ``..----------.....--.      sso.ss/  -ss-/ss.  :so++sss+   +sn- .oso- /ss+/+ss/ -ss+sss++ss+/+o-    -sr:/ss-  +ss`sss  ooo+osss-  sCs  :ss+` oss. ossooosss+ `oso//osso/
  *  -ssssssssssss.`--.`                  `.----------------.     sso /ss. os+ /ss.  `.----sss`  +sn+/ss+` :Dr+-.-+ss.-sss-```sss/-.`     -sn:`oso .ss: sss  `.---/ss+  sss:+ss:   oss. oss:```sss`:ss:  .ss+
  * .ssssssssssss+ ..                        `.--------------.    sso `os+-ss. /ss.  /sso++sss`  +siooss:  +sso+++ooo`-ss+    ./+osso:    -sa: -ss-+so  sss `+ss++oss+  s6s+sss.   oss. oss.   sss``oss++oso.
  * :+ossssssssss: `                           `------------..`   sso  -ssos/  /ss. .sss.`.sss-` +sn:`+ss/`-sso-.`..- -ss+   `.```:sso    -sb:  +soss.  sss /ss+``:sso.`sBs`-sss-  oss. oss.   sss``oso:::.`
  *   `-+ssssssss.                               .--------`       ss+   +sso`  /ss.  +3999++sss: /sg- `/ss+.-+sssooo+ .ss+   .osoosso-    -sy:  `sss/   oso .ossoo+osso.s9s  .+ss/ oss` +ss.   oss`.sssoooo+:`
  *    `+sssssss.                              ` .------`        ```   ````   ```   `...` ... ```     ````  `....`   ```    `....``      ```   ```    ```  `...` `..` ```    ``` ```  ```    ``` +ss---:/sso
  *     -sssssss:                              .. `----.                                                                                                                                       `sss:-.-:ss+
  *      `:ossssso                              .-. .----                                                                                                                                        ./+oooo++-`
  *    `..``-+ssss:                            `---` .----`         `.-::::-` .//-                                                                                                                  ````
  * `..-----.`.:+ss:                          `----- `------..`   `:osssoooo/ /ss:
  * `----------.`.-/:`                       .------` .------.   `+ss+-`````. /ss:``..`    ``...`    ``` `...`    ``..````    `...`
  *  `------------....`                    `.-------. `-----.    /sso         /ss/ossso/  /osssso+.  +o+/ossso- `/oooooooo/ -+ooooo+`
  *   `--.....---------...```       ```` `.---------. `...-.     oss/         /sso-.-sss- :----+ss+  oss+-.:s1s :ss:``:ss/.:ss/..-sso
  *            `.------------------..```.--------.`       `      +ss+         /ss:   +ss- -+o++osso  oss.  `s9s -ss+--/ss: ssso+++sss
  *              `.--------------.```.----------`                .sss/.`   `` /ss:   +ss-:ss+..:sso  oss.   s8s `+ssooo/-  oss/-.....
  *               `---------..````.------------.                  .ossso+++o+ /ss:   +ss--sso//+sss+-oss.   s4s -sso/:::-` .oss+///+:
  *               .----..``````......-----------                    .://+//:` .::.   .::` .://:.-//:`-::`   ::: :ss+++ooss: `-:////-`
  *               .`````....`        ``--------.`                                                              `sso````.sso
  *                  ``..-.            `-...``                                                                  /ossoooss+.
  *                                                                                                             `..--..`
  *
  *
  *  +++         .+++:    /++++++++/:.     .:/+++++/: .+++/`     .+++/  ++++.      ++++.     `-/++++++/:
  *  oooo         .ooo:    +ooo:--:+ooo/   :ooo/:::/+/  -ooo+`   .ooo+`  ooooo:     .o-o`   `/ooo+//://+:
  *  oooo         .ooo:    +ooo`    :ooo-  oooo`     `   .ooo+` .ooo+`   oooooo/`   .o-o`  .oooo-`
  *  oooo         .ooo:    +ooo`    -ooo-  -ooo+:.`       .ooo+.ooo/`    ooo:/oo+.  .o-o`  +ooo.
  *  oooo         .ooo:    +ooo.`..:ooo+`   `:+oooo+:`     `+ooooo/      ooo: :ooo- .o-o`  oooo
  *  oooo         .ooo:    +ooooooooo+:`       `-:oooo-     `+ooo/       ooo/  .+oo/.o-o`  +ooo.
  *  oooo         .ooo:    +ooo-...``             `oooo      /ooo.       ooo/   `/oo-o-o`  .oooo-
  *  oooo::::::.  .ooo:    +ooo`           :o//:::+ooo:      /ooo.       ooo/     .o-o-o`   ./oooo/:::/+/
  *  +ooooooooo:  .ooo:    /ooo`           -/++ooo+/:.       :ooo.       ooo:      `.o.+      `-/+oooo+/-
  *
  *  An open-source mouth operated sip and puff joystick that enables people with limited hand function to emulate a mouse on their computer and/or smartphone.
*/
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

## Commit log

2017-02-06 Created hardware directory for STL files
    [MMC LipSync Button.STL, MMC LipSync Front Housing.STL, MMC LipSync Joystick Base.STL, MMC LipSync Joystick Front Plate.STL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]
2017-02-18 Added Eagle PCB layout files version 2.5
    [LipSync_Interface_Board.brd, LipSync_Interface_Board.sch]
2017-02-18 Added LipSync FSR Arduino code version 2.4 (Jan 28th ) FSR_Fast_Load
    [LipSync_Interface_Board.brd, LipSync_Interface_Board.sch, MMC LipSync Button.STL, MMC LipSync Front Housing.STL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]
2017-02-18 Changed directory naming convention
    [LipSync_Interface_Board.brd, LipSync_Interface_Board.sch, MMC LipSync Button.STL, MMC LipSync Front Housing.STL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]
2017-02-25 Changed naming conversion for STL files
    [LipSync_Button.STL, LipSync_Front_Housing.STL, LipSync_Joystick_Base.STL, LipSync_Joystick_Front_Plate.STL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]
2017-02-25 Changed naming conversion for Arduino code
2017-03-04 Updated STL Files
    [LipSync_Button.STL, LipSync_Front_Housing.STL, LipSync_Joystick Front_Plate.STL, LipSync_Joystick_Base.STL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]
2017-03-10 LipSync Components in CSV format
    [LipSync_BOM.csv]
2017-03-10 Updated list of LipSync Components
    [LipSync_BOM.csv, LipSync_BOM.xlsx]
2017-03-11 Added Instructions manual for assembling a LipSync
2017-03-29 Updated Assembly Manual V.1.21
2017-04-06 Updated parts list
    [LipSync_BOM.csv, LipSync_BOM.xlsx]
2017-05-18 This is the modified LipSync_Joystick_Base .STL file
    [LipSync_Joystick_Base.STL]
2017-06-13 Updated Assembly Manual 1.41 and Startup guide.
2017-06-13 Updated Assembly Manual 1.41
2017-06-28 Updated STL files to V2.2d
    [LipSync Joystick Stand.STL, LipSync_Front_Housing.STL, LipSync_Joystick_Base.STL, LipSync_Joystick_Front.STL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]
2017-07-24 Corrected mesh quality issues for Front Housing
    [LipSync_Front_Housing.STL]
2017-10-02 Added Mounting Document
2017-10-26 Updated BOM file ( October 25,2017 )
    [LipSync_BOM.csv, LipSync_BOM.xlsx]
2017-12-13 Updated BOM file ( December 13,2017 )
    [LipSync_BOM.xlsx]
2018-01-05 Updated PCB eagle files to version 2.7
    [LipSync_Interface_Board.brd, LipSync_Interface_Board.sch]
2018-03-02 Updated BOM file (March 2, 2018)
    [LipSync_BOM.csv]
2018-03-12 Updated BOM file (March 12, 2018)
    [LipSync_BOM.csv, LipSync_BOM.xlsx]
2018-05-08 Assembly Manual
2018-06-19 Updated BOM file (June 19, 2018)
    [LipSync_BOM.xlsx]
2018-07-03 Updated BOM file (July 3, 2018)
    [LipSync_BOM.csv]
2018-07-10 Updated Joystick PCB ( Reconnected a trace )
    [LipSync_Interface_Board.brd, LipSync_Interface_Board.sch]
2018-11-13 Added the pdf version of Lipsync boards and schematics
2019-08-13 Update BOM (2019-Aug-13)
    Updated link for Lee Springs
    [LipSync_BOM.csv, LipSync_BOM.xlsx]
2019-09-17 Updated BOM file
    [LipSync_BOM.csv, LipSync_BOM.xlsx]
2019-09-20 Added the updated LipSync Manual, LipSync User Guide, LipSync Startup Guide, and LipSync BOM File.
    [LipSync_BOM.csv, LipSync_BOM.xlsx]
2019-10-01 Update to V2.3
    - The shell is slightly longer and the rear portion is slightly wider to accommodate a greater range of USB cables. The cut-out near the mounting hole is also larger and longer to prevent the threade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
    - A recess has been added to the bottom to provide a less conspicuous location to apply any labelling.
    - The rear portion of the shell is larger and has greater surface area which should help mitigate any bed adhesion issues.
    - The cylindrical portions that house the springs have been lengthened and a catch was added that should retain the springs once they are pressed in. These changes should help m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
    [LipSync_Button.stl]
2019-10-01 Added PCB files Version 2.71 with updated MMC Logo.
    [LipSync_Interface_Board.brd, LipSync_Interface_Board.sch]
2019-10-01 Updated PCB version number in readme file.
2019-11-07 Binary version of stl to save space.
    [LipSync_Rear_Housing.STL]
2020-04-15 Added PCB board gerber files.
    [LipSync_Interface_Board.brd, LipSync_Interface_Board.sch, LipSync_Joystick_Board.brd, LipSync_Joystick_Board.sch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]
2020-04-15 Updated readme file
    Added the links to PCB board gerber files.
2020-05-08 PCB Fabricaiton Manual
2020-05-08 PCB Fabrication Manual
2021-05-12 Rename Print Settings to 3D Print Settings
2021-05-12 Rename LipSync Joystick Stand to LipSync Joystick Jig
    [LipSync_Joystick_Jig.STL]
2021-05-12 Update LipSync_Rear_Housing.STL
    - Add light pipe hole for Bluetooth Module
    - Add visual icon to Bluetooth Light Pipe and status indicator
    - Extend USB cable slot to provide more clearance between cable and mounting hardware
    - Add additional cable slot for Switch Input cables.
    - Add fillets to bottom circuit board support to reduce stress concentration and improve printability
    [LipSync_Rear_Housing.STL]
2021-05-17 Add dynamic light change to sip and puff counter
    As puff or sip counts increment, turns LED color when count is reached to indicate to user when they can release.
    Puff(off) -> Time -> Med Puff/ Red -> Time -> Long sip / off
    Sip (off) -> Time -> Med sip / Green-> Time -> Long sip / off
2021-05-19 re-enable skipChange
    [LipSync_BOM.xlsx]
2021-05-20 Update LipSync_Rear_Housing.STL
    Final update for V3.0 ready for print testing.
    -extended circuit board slot
    -removed label groove
    -update light pipe icons
    [LipSync_Rear_Housing.STL]
2021-05-25 Swap LED_1 with LED_GREEN and LED_2 with LED_RED
2021-06-01 Updated new API endpoints to use the new serial print out functions
2021-06-01 Added print response function calls to raw and debug modes
2021-06-02 Added new print function for API
2021-06-03 Updated print functions and added comments
2021-07-30 Added led clear to scroll function
2021-08-18 Update mounting document name
2021-08-18 Optimize and expand unused pin setting
2021-08-18 Update LipSync_Firmware.ino
    Remove unnecessary code from ledBlink
2021-09-01 Move documentation
    [LipSync_BOM.csv, LipSync_BOM.xlsx]
2021-09-01 Documentation Update
    [LipSync_BOM.csv, LipSync_BOM.xlsx]
2022-06-09 Updated documentation
    [LipSync_BOM.csv, LipSync_BOM.xlsx]
2022-06-09 Added STL with correct extension
    [LipSync_Rear_Housing.STL]
2022-06-16 Updated documents
    [LipSync_BOM.csv, LipSync_BOM.xlsx]

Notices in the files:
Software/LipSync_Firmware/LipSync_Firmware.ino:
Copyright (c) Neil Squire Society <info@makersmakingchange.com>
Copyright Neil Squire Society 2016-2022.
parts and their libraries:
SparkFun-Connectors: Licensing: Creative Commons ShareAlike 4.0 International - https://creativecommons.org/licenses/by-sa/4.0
